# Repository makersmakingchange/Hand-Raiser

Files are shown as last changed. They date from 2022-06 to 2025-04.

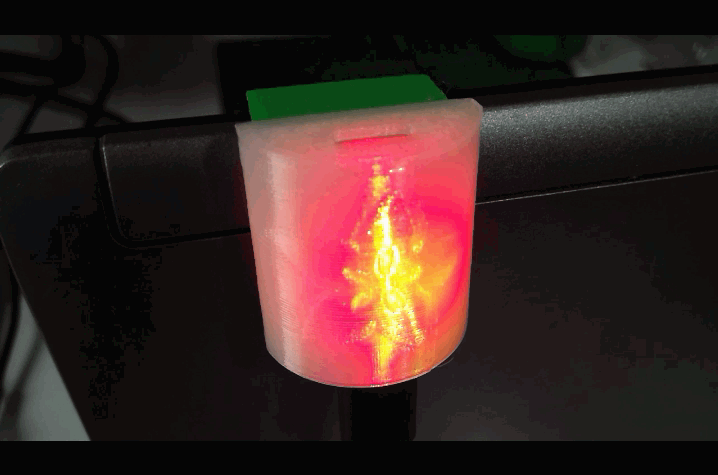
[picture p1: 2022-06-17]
Photos/Light on.PNG

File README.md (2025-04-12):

# Hand-Raiser
An assistive device used to catch the attention of a professor: an alternative to a student having to raise their hand.

Light on

## More info at
- [Makers Making Change Project Page]( https://makersmakingchange.com/project/hand-raiser/)
- [Adafruit Learning Guide](https://learn.adafruit.com/AT-Hand-Raiser)

## Getting Started
1. How to build this device

All of the files and instructions required to build the Hand-Raiser are contained within this repository. Refer to the Maker Checklist below.

2. How to request a build of this device

If you would like to obtain a Hand-Raiser but do not have the skills or equipment to do so, you may submit a build request through the [MMC Library Page](  https://makersmakingchange.com/project/hand-raiser/). The requestor is responsible for the cost of materials and any shipping.

3. How to build this device for someone else

If you have the skills and equipment to build this device, and would like to donate your time to create the switch for someone who needs it, visit the [MMC Maker Wanted](https://makersmakingchange.com/maker-wanted/) section.

## Files

### Documentation
| Document                     | Version | Link                                                                                  
|------------------------------|---------|--------------------------------------------------------------------------------|
| Maker Checklist              | 1.0     | [Maker Checklist](/Documentation/Hand-Raiser_Maker_Checklist.pdf)         |
| Bill of Materials            | 1.0     | [BOM](/Documentation/Working_Documents/Hand-Raiser_BOM.xlsx)                                |
| 3D Printing Guide            | 1.0     | [3D Printing Guide](Documentation/Hand-Raiser_3D_Print_Guide.pdf)      |
| Assembly Guide               | 1.0     | [Assembly Guide](/Documentation/Hand-Raiser_Assembly_Guide.pdf)           | 
| Maker Checklist              | 1.0     | [Maker Checklist](/Documentation/Hand-Raiser_Maker_Checklist.pdf)         |
| Adding Additional Colours    | 1.0     | [Adding Additional Colours](/Documentation/Hand-Raiser_How_to_Add_Additional_Colours.pdf)                  |
| User Quick Guide             | 1.0     | [User Guide](/Documentation/Hand-Raiser_User_Guide.pdf)                  |

## Attribution 

This device was designed by AT Makers.
The code for this device was written by Bill Binko and is licensed under the MIT license.
The Hand-Raiser 3D printed housing was designed by AT Makers and is licensed under the Creative Commons - Attribution - Non-Commercial - Share Alike license.
Documentation for this device was created by Neil Squire / Makers Making Change licensed under the CC-BY-SA 4.0 license.

## License 
Everything needed or used to design, make, test, or prepare the Hand Raiser is licensed under the CERN 2.0 Permissive license <https://ohwr.org/project/cernohl/wikis/Documents/CERN-OHL-version-2> (CERN-OHL-P) . 

Accompanying material such as instruction manuals, videos, and other copyrightable works that are useful but not necessary to design, make, test, or prepare the Hand Raiser are published under a Creative Commons Attribution-ShareAlike 4.0 license <https://creativecommons.org/licenses/by-sa/4.0/> (CC BY-SA 4.0) 

 ----

<!-- ABOUT MMC START -->
## About Makers Making Change
[Makers Making Change Logo](https://www.makersmakingchange.com/)

Makers Making Change is a program of [Neil Squire](https://www.neilsquire.ca/), a Canadian non-profit that uses technology, knowledge, and passion to empower people with disabilities.

Makers Making Change leverages the capacity of community based Makers, Disability Professionals and Volunteers to develop and deliver affordable Open Source Assistive Technologies.

 - Website: [www.MakersMakingChange.com](https://www.makersmakingchange.com/)
 - GitHub: [makersmakingchange](https://github.com/makersmakingchange)
 - Bluesky: [@makersmakingchange.bsky.social](https://bsky.app/profile/makersmakingchange.bsky.social)
 - Instagram: [@makersmakingchange](https://www.instagram.com/makersmakingchange)
 - Facebook: [makersmakechange](https://www.facebook.com/makersmakechange)
 - LinkedIn: [Neil Squire Society](https://www.linkedin.com/company/neil-squire-society/)
 - Thingiverse: [makersmakingchange](https://www.thingiverse.com/makersmakingchange/about)
 - Printables: [MakersMakingChange](https://www.printables.com/@MakersMakingChange)

### Contact Us
For technical questions, to get involved, or to share your experience we encourage you to [visit our website](https://www.makersmakingchange.com/) or [contact us](https://www.makersmakingchange.com/s/contact).
<!-- ABOUT MMC END -->

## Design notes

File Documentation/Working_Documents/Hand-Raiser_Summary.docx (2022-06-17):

### Title

Hand-Raiser

### Subtitle

An assistive device used to catch the attention of a professor: an alternative to a student having to raise their hand.

### Device Specifications

Build Time:

< 1hr

1-4 hr

5-10hr

>10hr

Cost:

$0 - $10

$11 - $25

$26 - $50

$51 - $100

$101 - $250

$250+

Stage: Recently Added

Skills: 3D Printing, Software

Need: Mobility

Disability: Mobility/Physical

Difficulty: Beginner

License:

Usages: Aids for Daily Living (ADL), Mobility, Communications Aids (AAC)

Type:

Designer: AT Makers

## Device Details

### Overview

The Hand-Raiser is an assistive device intended to be used to catch the attention of a professor without a student having to raise their hand. This device would be beneficial for someone who has difficulty or is unable to raise their hand for an extended period of time.

### Usage

The Hand-Raiser works by flashing it's light according to the incoming requests through the USB connection. The Hand-Raiser includes a set of Windows Shortcuts that can be used to change the LED by just double clicking on it.

### Compatibility

The Hand-Raiser can work with any PC, Mac, Android, or Raspberry Pi with a USB port.

### Cost

The Hand-Raiser costs approximately $15.

### Build Instructions

#### A set of build instructions can be found linked above in the Assembly Guide.

#### Skills Required

- 3D Printing Skills
- Programming

### Time Required

- Total print time: 70 minutes
- Assembly Time: 10 minutes

#### Tools

- 3D Printer
- Computer with USB port

#### Components

- 1x Adafruit Trinket - Link (https://www.adafruit.com/product/3500)
- 1x USB Cable - USB A to micro-B - Link (https://www.adafruit.com/product/592)

### 3D Printing

All components can be printed with no support at 20% infill with a 0.2mm layer height. There are 3 pieces to the enclosure: a back plate, a hanging hook, and a faceplate.

- 1x Back Plate
- 1x Hanging Hook
- 1x Faceplate - This piece must be printed with translucent filament.

Note that there are several versions of the hook and the faceplate, but you only need one of each.

### Attribution

The code for this device was written by Bill Binko and is licensed under the MIT license.

The Hand-Raiser 3D printed housing was designed by AT Makers (http://atmakers.org/2020/01/handraiser-light/) and is licensed under the Creative Commons - Attribution - Non-Commercial - Share Alike license.

Documentation for this device was created by Neil Squire / Makers Making Change licensed under the CC-BY-SA 4.0 license.

© 2022 by Neil Squire / Makers Making Change. This work is licensed under the CC BY SA 4.0 License: http://creativecommons.org/licenses/by-sa/4.0 Files available at https://makersmakingchange.com/project/hand-raiser/ Page 1 of 2

V1.0 | MAY 2021 Hand-Raiser Summary

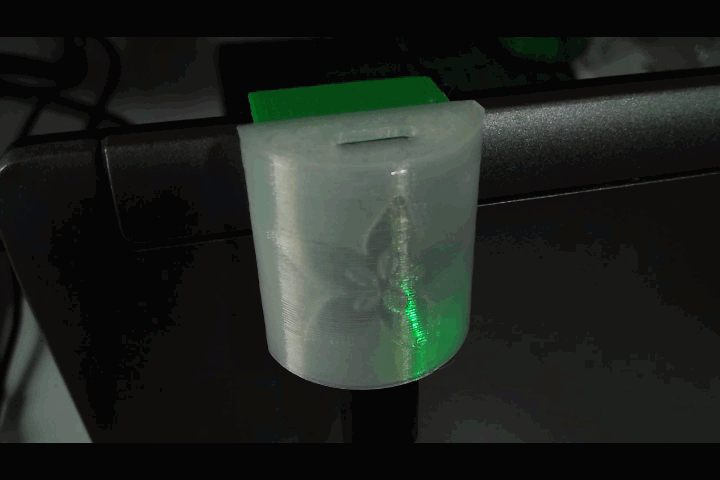
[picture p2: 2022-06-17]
Photos/trinket_Light3.gif

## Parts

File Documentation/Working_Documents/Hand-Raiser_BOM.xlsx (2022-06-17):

Device: Hand-Raiser |  | Total Cost | Total Print time (hr) | Total filament (g)
Version: V1.0 | Date Created: MAY 2022 | $12.15 | 1.17 | 10
Commercial Parts:
Part type (Electrical. Mechanical, Sanitization, ect) | Part Name | Quantity Needed | Pkg Quantity | Price per package | Price per Unit | Price for qty needed | Link
Microcontroller Board | Adafruit Trinket M0 | 1 | 1 | $8.95 | $8.95 | $8.95 | Adafruit Trinket M0 - for use with CircuitPython & Arduino IDE : ID 3500 : $8.95 : Adafruit Industries, Unique & fun DIY electronics and kits (https://www.adafruit.com/product/3500)
USB Cable | USB A to Micro-B | 1 | 1 | $2.95 | $2.95 | $2.95 | USB cable - USB A to Micro-B [3 foot long] : ID 592 : $2.95 : Adafruit Industries, Unique & fun DIY electronics and kits (https://www.adafruit.com/product/592)
3D Printed Parts ESTIMATED PRICING USING 1KG ROLL COST: | $25.00
Part | Description | Quantity Needed | TOTAL Mass (g) | Estimated Price | Print Time (Min) | Link
Snap Back | Piece that the micro controller snaps onto | 1 | 3 | $0.07 | 13
Snap Hanger | Piece used to hang the device | 1 | 3 | $0.07 | 21
Face Plate | Clear piece that covers LED light | 1 | 4 | $0.10 | 36
 |  |  | Total Print Cost: | $0.25
Tools for Assembly
Computer with Windows
Alternatives (if there are other sources for some parts link them below)
Part and description | Link

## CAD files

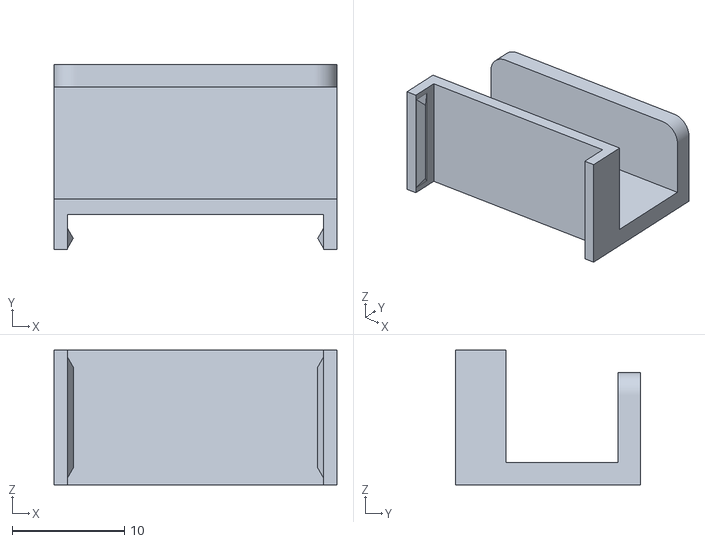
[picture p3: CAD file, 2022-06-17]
Build_Files/Snap_Hanger.stl
25.2 x 16.5 x 12.0

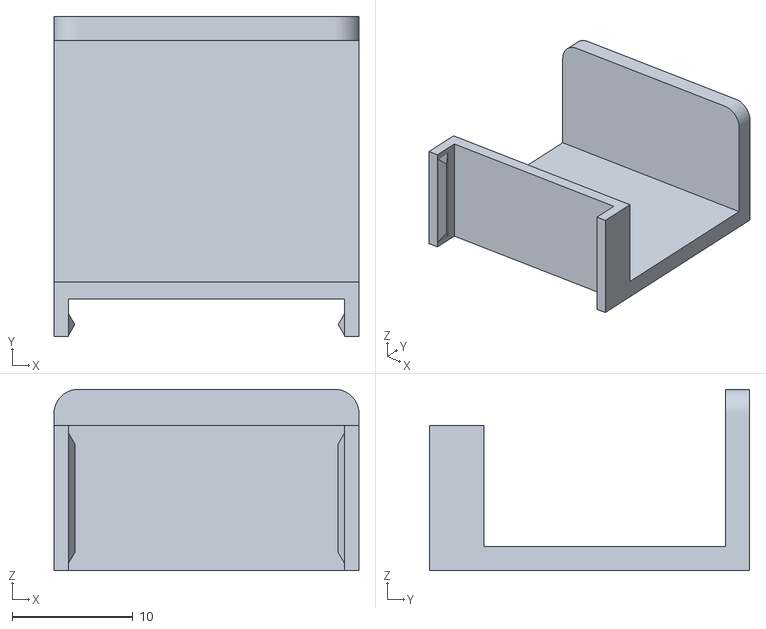
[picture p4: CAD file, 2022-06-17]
Build_Files/Snap_Hanger_20mm.stl
25.2 x 26.5 x 15.0

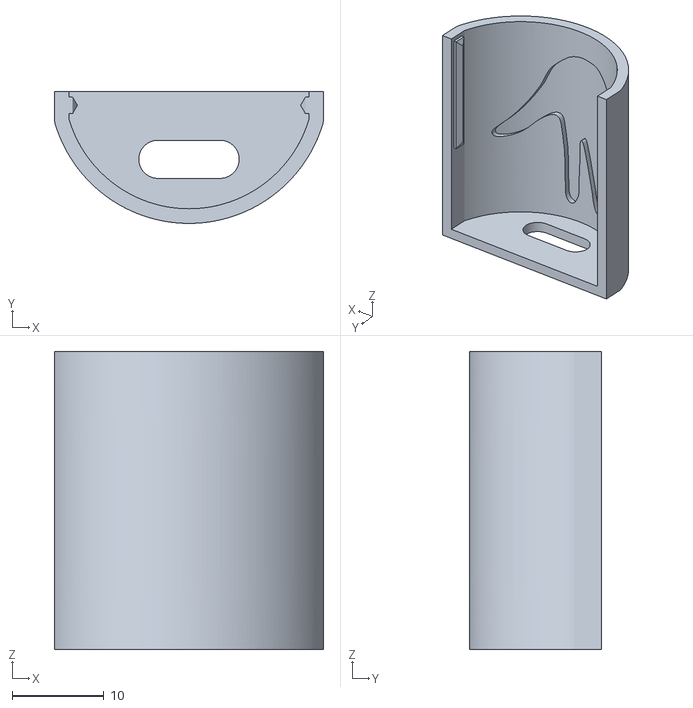
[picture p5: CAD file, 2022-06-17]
Build_Files/Faceplate-Hand.stl
29.4 x 14.4 x 32.6

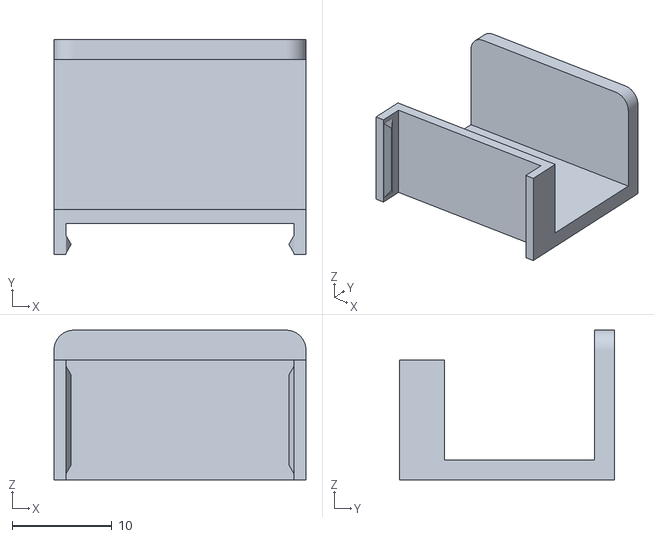
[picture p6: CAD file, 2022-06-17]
Build_Files/Snap_Hanger_15mm.stl
25.2 x 21.5 x 15.0

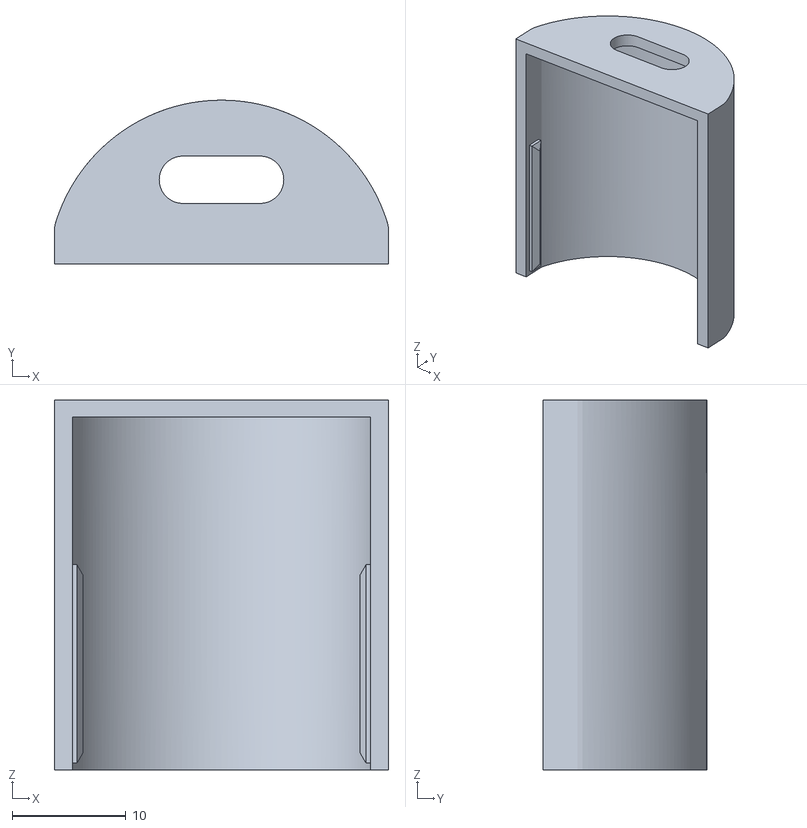
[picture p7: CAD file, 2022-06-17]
Build_Files/Faceplate-Blank.stl
29.4 x 14.4 x 32.6

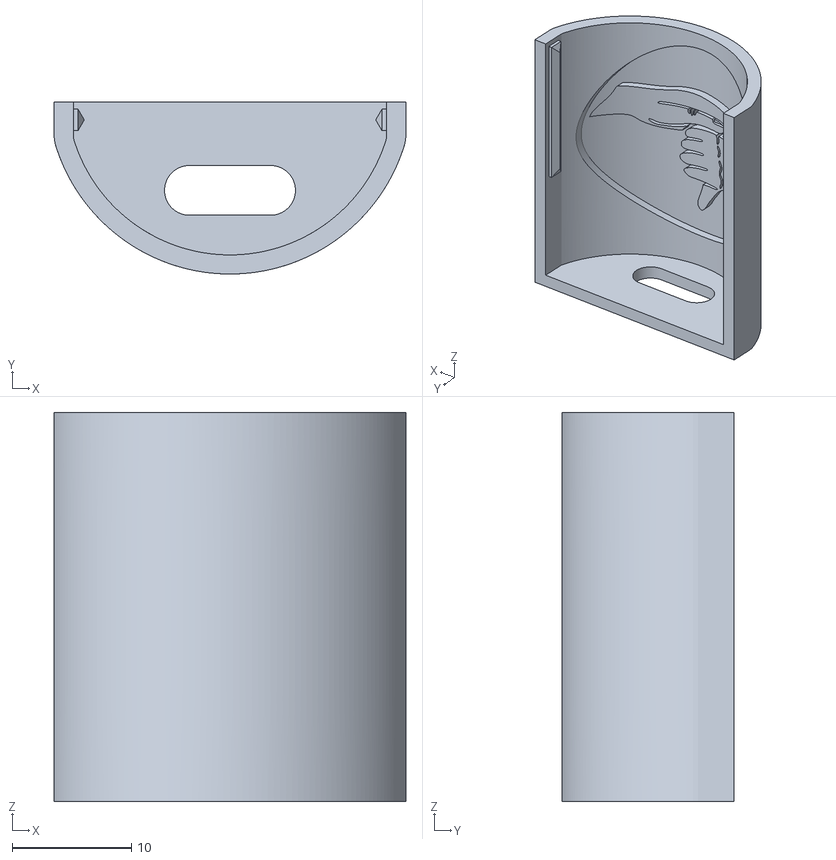
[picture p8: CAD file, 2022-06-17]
Build_Files/Faceplate-ATMakers.stl
29.4 x 14.4 x 32.6

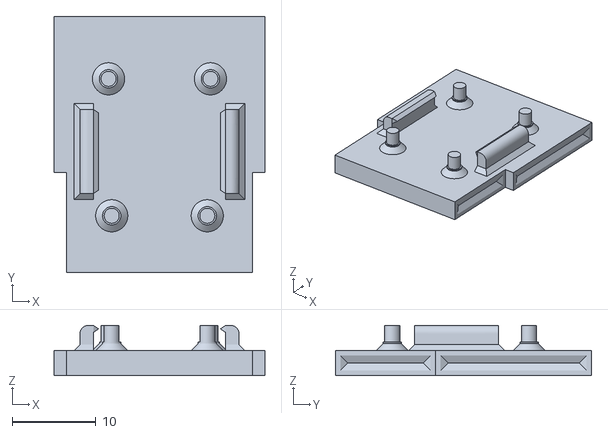
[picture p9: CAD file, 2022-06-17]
Build_Files/Snap_Back.stl
25.2 x 30.7 x 6.00

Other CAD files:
Build_Files/Faceplate-Adafruit.stl
Design_Files/Little_Handraiser.f3d

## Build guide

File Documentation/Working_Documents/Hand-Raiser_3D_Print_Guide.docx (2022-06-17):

# 3D Printing Summary

Metrics | HandRaiser with 15mm Snap Hanger | HandRaiser with 20mm Snap Hanger
Total Print Time (min) | 69 | 69
Total Number of Components | 3 | 3
Typical Total Mass (g) | 10 | 10
Typical Number of Print Setups | 2 | 2

# 3D Printing Settings

Print File Name | Qty | Total Print Time (hr:min) | Mass (g) | Infill (%) | Support (Y/N) | Layer Height/ Nozzle Diameter(mm) | Notes (orientation, special settings, etc)
Snap_Back.stl | 1 | 0:12 | 3 | 20 | N | 0.2/0.4 | Print in orientation given in STL
Snap_Hanger.stl (10mm) | 1 | 0:17 | 3 | 20 | N | 0.2/0.4 | Print in orientation given in STL
Snap_Hanger_15mm.stl | 1 | 0:21 | 3 | 20 | N | 0.2/0.4 | Print in orientation given in STL
Snap_Hanger_20mm.stl | 1 | 0:21 | 3 | 20 | N | 0.2/0.4 | Print in orientation given in STL
Faceplate-Blank.stl | 1 | 0:36 | 4 | 20 | N | 0.2/0.4 | Print in orientation given in STL
Faceplate-ATMakers.stl | 1 | 0:36 | 4 | 20 | N | 0.2/0.4 | Print in orientation given in STL
Faceplate-Hand.stl | 1 | 0:36 | 4 | 20 | N | 0.2/0.4 | Print in orientation given in STL
Faceplate-Adafruit.stl | 1 | 0:36 | 4 | 20 | N | 0.2/0.4 | Print in orientation given in STL

# Post-Processing

The Hand-Raiser is printed without supports; hence no post-processing is required.

# Customization Options

The Hand-Raiser can be printed with different sized hangers depending on which size works best for the user. There are .stl files for a 10mm (1), 15mm (2) and a 20mm hanger (3), but the. f3d file can be modified to accommodate other sized hangers if needed. The hand raiser can also be printed with different designs on the faceplate. The faceplate can be printed with an outline of a hand (4), an adafruit (5), the ATMakers symbol (6) or plain (7) as faintly shown below. Other customizations include printing the device in different colours.

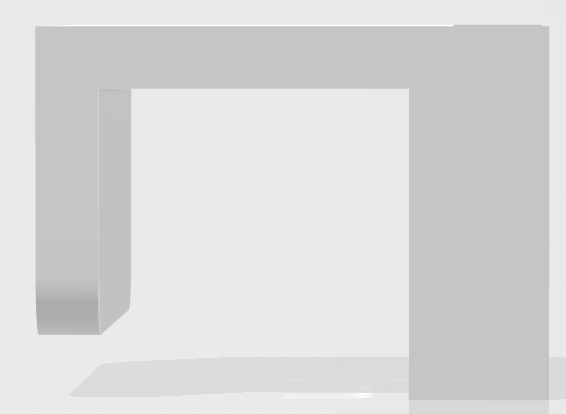
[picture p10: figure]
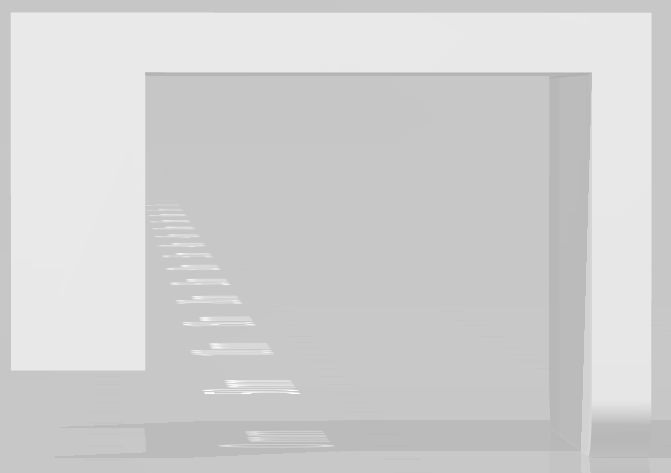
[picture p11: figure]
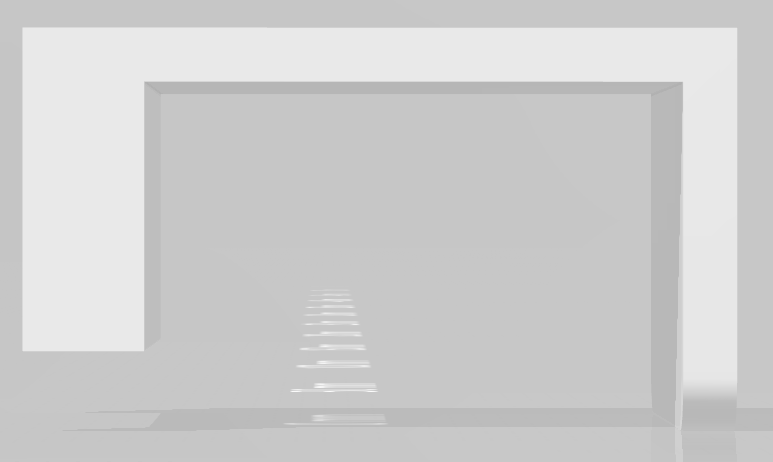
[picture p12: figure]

(1) 10cm Hanger | (2) 15mm Hanger | (3) 20mm Hanger

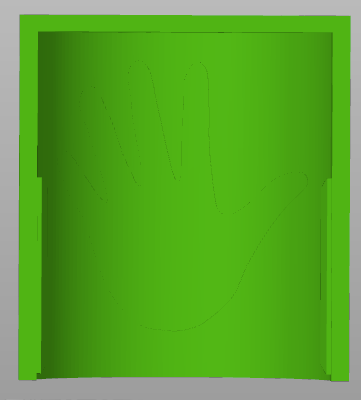
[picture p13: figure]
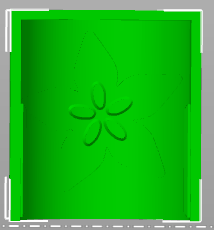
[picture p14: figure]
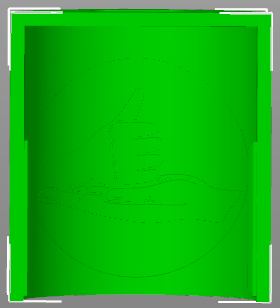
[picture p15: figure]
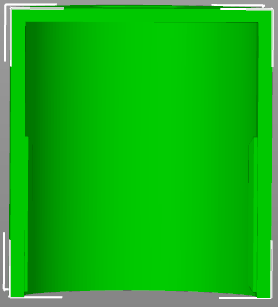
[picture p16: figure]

| (4) Hand | (5) Adafruit | (6) ATMakers | (7) Blank

# Examples of Quality Prints

Below is a picture of what quality is expected from printing the device.

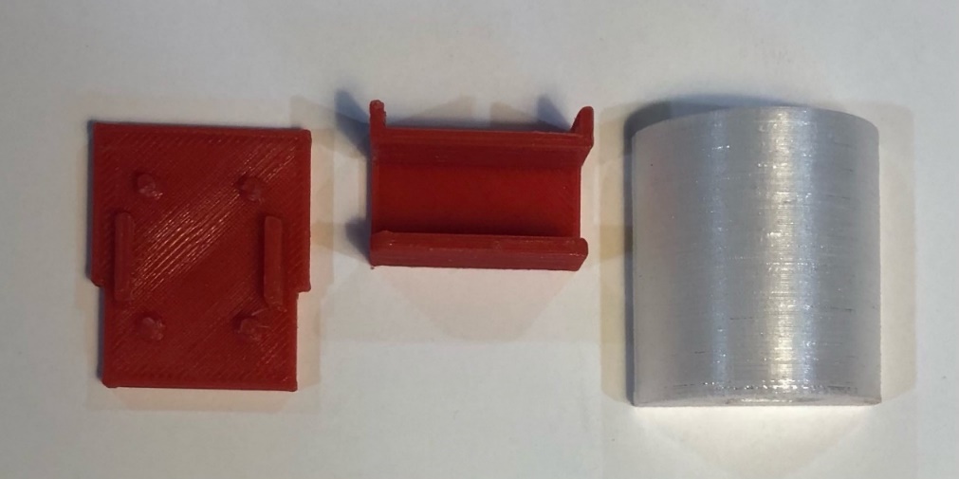
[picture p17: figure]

© 2022 by Neil Squire / Makers Making Change. This work is licensed under the CC BY SA 4.0 License: http://creativecommons.org/licenses/by-sa/4.0 Files available at https://makersmakingchange.com/project/hand-raiser/ Page 1 of 2

V1.0 | MAY 2022 Hand-Raiser 3D Printing Guide

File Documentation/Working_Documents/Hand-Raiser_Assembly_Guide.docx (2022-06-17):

# Required Components

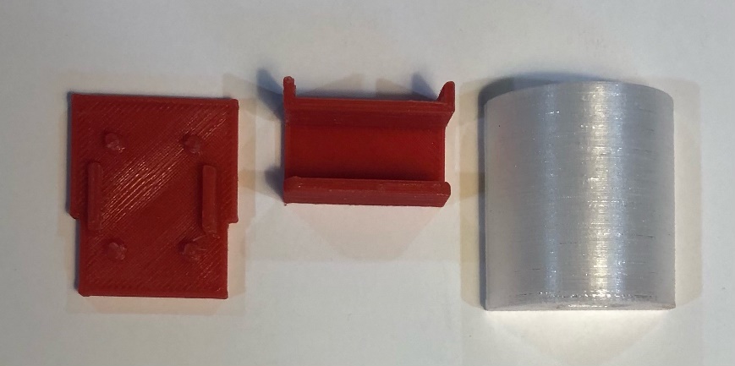
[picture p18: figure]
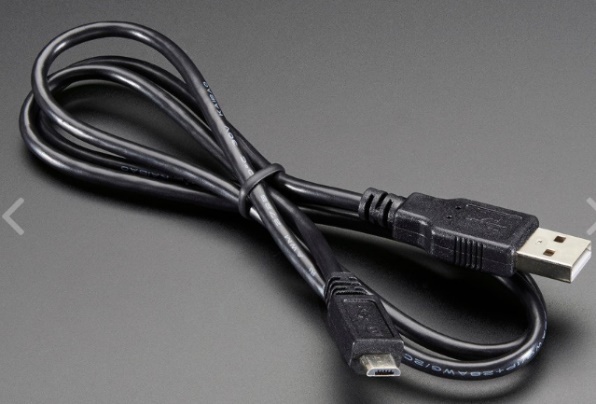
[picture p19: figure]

2 3 1 4 | BOM 1 1x 3D Printed Snap Back 2 1x 3D Printed Snap Hanger 3 1x 3D Printed Face Plate 4 1x USB Cable – USB A to USB Micro

# Required Tools

- Computer with Windows.

# Programming the Trinket

## Step 1

Download the HandRaiser.UF2 file. https://github.com/ATMakersOrg/Little-HandRaiser/raw/master/LittleHandRaiser.UF2

## Step 2

Carefully plug the Trinket into your USB port in your computer.

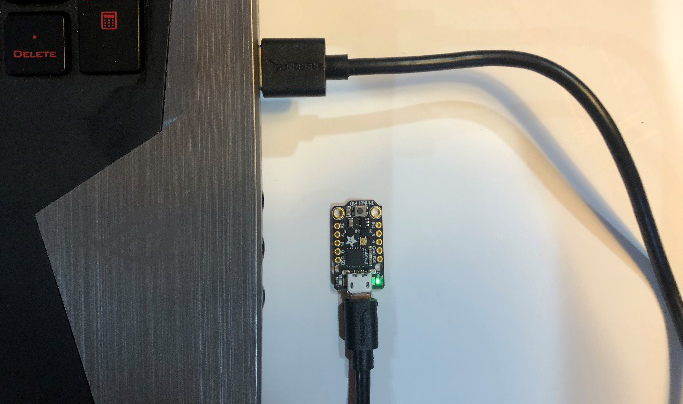
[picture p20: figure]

## Step 3

Put the Trinket in Bootloader Mode by double clicking the Reset Button. The LED light should blink green.

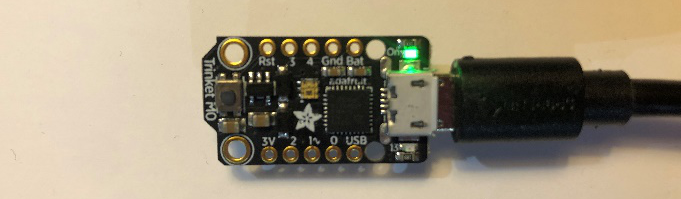
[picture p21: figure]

## Step 4

Locate the new drive named TRINKETBOOT (F:).

## Step 5

Copy the HandRaiser.UF2 file to that drive. The Trinket will restart, and the drive should be renamed to CIRCUITPY.

## Step 6

The Windows Commands can now be used to activate the device.

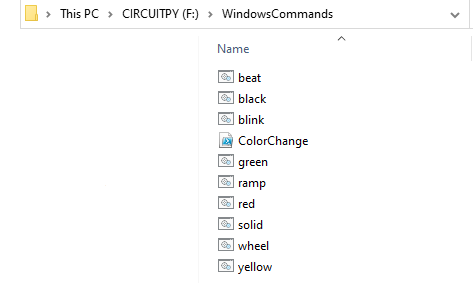
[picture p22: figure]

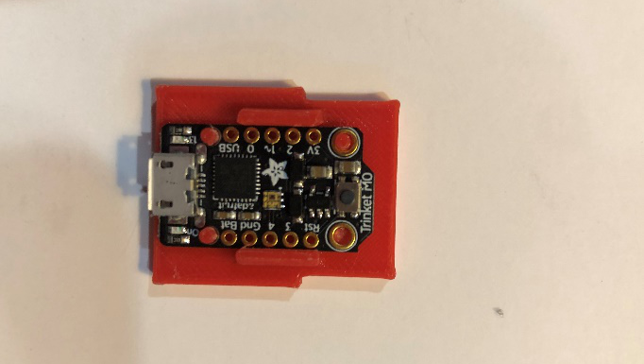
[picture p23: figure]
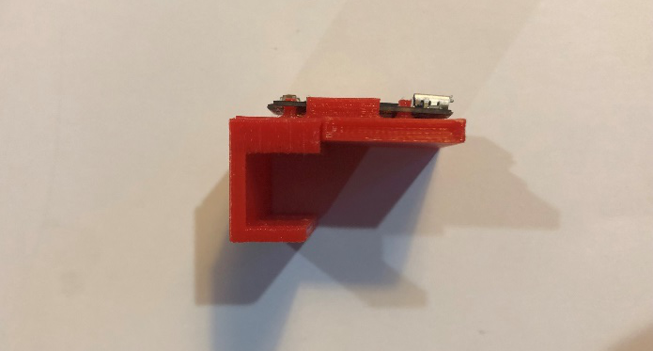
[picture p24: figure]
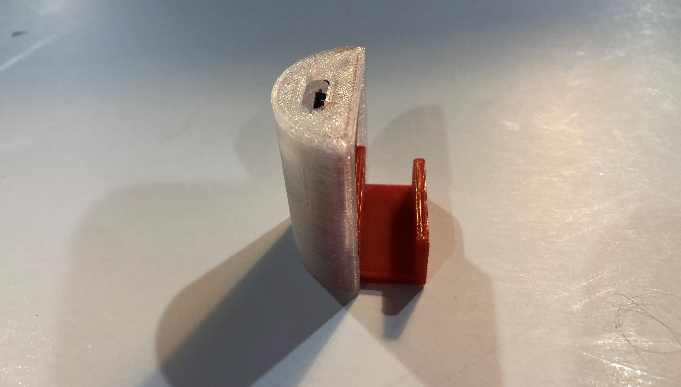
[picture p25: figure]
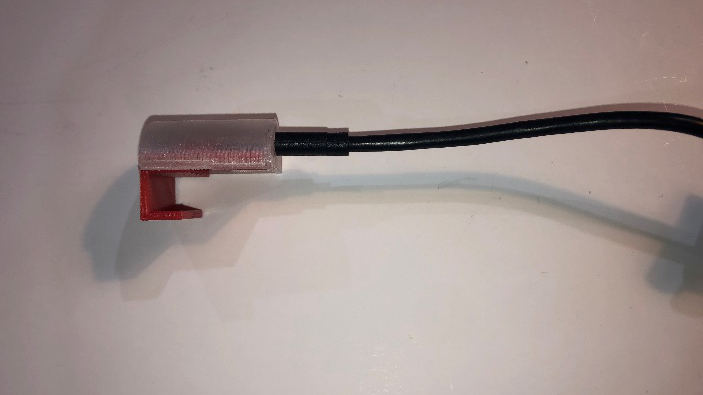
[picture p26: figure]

Assembly Instructions Step 1 Align the 4 holes on the Trinket M0 with the Snap Back. Make sure the micro-USB port is pointed towards the wider end of the print. Firmly press it on. Step 2 Snap on the Hanger onto the Snap Back using the snap-fit grooves. Step 3 Snap on the cover. Make sure the end with the hole aligns with the micro-USB port. Step 4 Carefully plug the micro-USB cable into the Trinket.

© 2022 by Neil Squire / Makers Making Change. This work is licensed under the CC BY SA 4.0 License: http://creativecommons.org/licenses/by-sa/4.0 Files available at https://makersmakingchange.com/project/hand-raiser/ Page 1 of 1

V1.0 | MAY 2022 Hand-Raiser ASSEMBLY GUIDE

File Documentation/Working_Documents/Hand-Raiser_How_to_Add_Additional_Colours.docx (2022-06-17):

# Overview

Once the Hand-Raiser is programmed, it automatically comes with red, yellow, and green light shortcuts. If the user wants additional colour shortcuts added onto the device, this document can be used to explain how to do so with a Windows computer.

# Adding Additional Colours on Windows

## Step 1

In the search bar, locate and open the Notepad App.

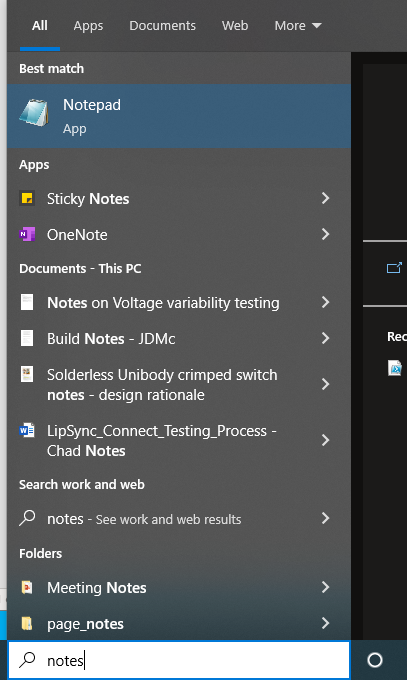
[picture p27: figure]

## Step 2

Type powershell -executionpolicy bypass -File "ColorChange.ps1" "#" into the NotePad as well the 6 digit Hex code following the # of the colour you are trying to achieve. A hex code for any colour can be found here: link (https://www.rapidtables.com/web/color/html-color-codes.html). For example, the #ff00ff below is the Hex code for a pink.

## Step 3

Next, in the top left corner of the Notepad, press File -> Save as. The window below should pop up. Make sure you save this short cut in CIRCUITPY (F:) -> WindowsCommands. When naming the file, make sure you name it with a .bat following the name. For example, shown below is the file named pink.bat. Next, ensure under the Encoding tab that ANSI is selected.

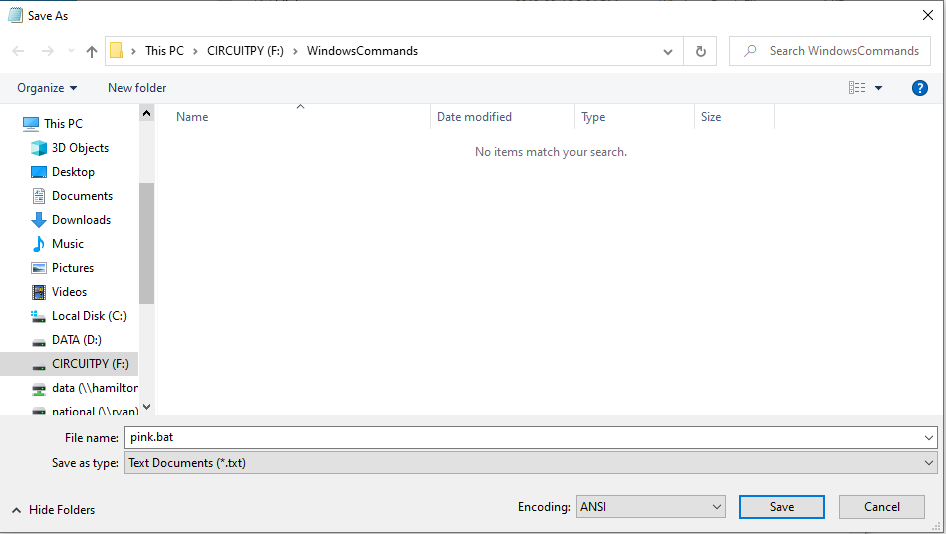
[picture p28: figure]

## Step 4

Open up Files -> CIRCUITPY (F:) -> WindowsCommands to see if the new colour is there. Next, you can double click on the colour to check that it works. Sometimes the hex code colours do not come out exactly how they appear online and will have to be modified to achieve the colour that you are looking for.

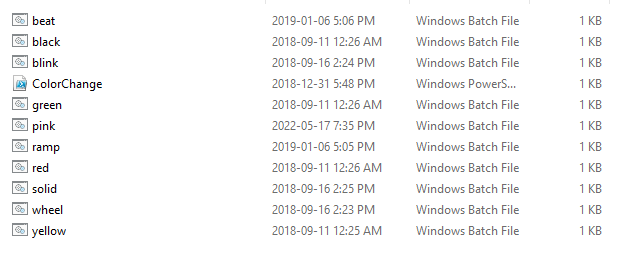
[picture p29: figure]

© 2022 by Neil Squire / Makers Making Change. This work is licensed under the CC BY SA 4.0 License: http://creativecommons.org/licenses/by-sa/4.0 Files available at https://makersmakingchange.com/project/hand-raiser/ Page 1 of 4

V1.0 | MAY 2022 Hand-Raiser hOW TO ADD ADDITIONAL COLOURS

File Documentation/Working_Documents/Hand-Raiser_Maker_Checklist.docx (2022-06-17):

# Maker To Do List

- Ask the requestor if they want any customizations to the device (e.g., colour, which size hanger they want, which design on the faceplate they want, etc.)
- Determine the cost of materials and relay this cost to the user before printing to ensure the requester is comfortable with the price.
- Tell the user that red, yellow, and green LED shortcuts come programmed on the Hand-Raiser. Ask the user if there are any additional colours that they would like programmed. They can have any colors that are in the Color Hexadecimal System. If they want to pick custom colors, send them this link to the Hex Calculator: Colors HEX (w3schools.com) (https://www.w3schools.com/colors/colors_hexadecimal.asp).
- Order the Adafruit Trinket and USB Cable.
- Make sure that you have a translucent filament as well as a regular filament.
- Build the Hand-Raiser.
- Program the Adafruit Trinket.
- Add shortcuts to any additional colours requested by the user. Test the new colours to ensure they are close to what the user expected from the Hex Calculator. Not every colour translates perfectly so you might have to tweak the Hex code.

# Items to Give to User

- User Guide.
- Hand-Raiser.
- USB cable.

© 2022 by Neil Squire / Makers Making Change. This work is licensed under the CC BY SA 4.0 License: http://creativecommons.org/licenses/by-sa/4.0 Files available at https://makersmakingchange.com/project/hand-raiser/ Page 1 of 1

V1.0 | MAY 2022 Hand-Raiser Maker Checklist

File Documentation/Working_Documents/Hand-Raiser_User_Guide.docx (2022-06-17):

## Introduction

The Hand-Raiser is an assistive device used to catch the attention of a professor without a student having to raise their hand. This device would be beneficial for someone who has difficulty or is unable to raise their hand for an extended period of time.

## Features

This device can flash different colour LED lights at different brightness levels and in different patterns. In the below figures, the LED light is red and is flashing on (A) and off (B).

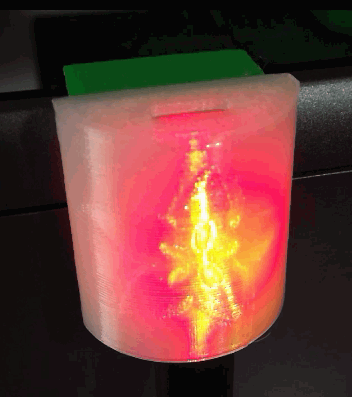
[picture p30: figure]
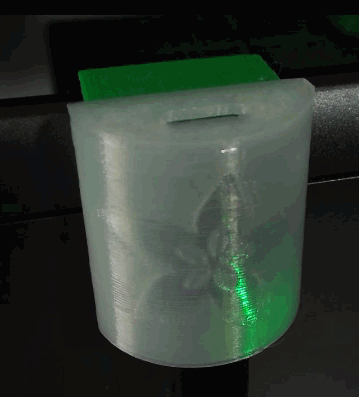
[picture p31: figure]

A | B

## Usage

The Hand-Raiser works by listening to the incoming requests through the USB connection. The Hand-Raiser includes a set of Windows Shortcuts that can be used to change the LED by just double clicking on them.

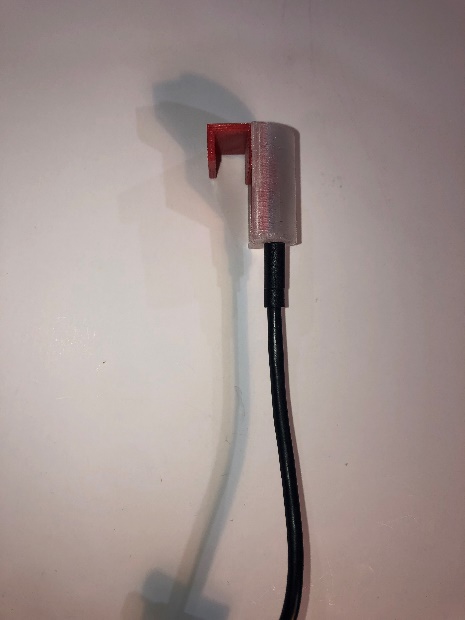
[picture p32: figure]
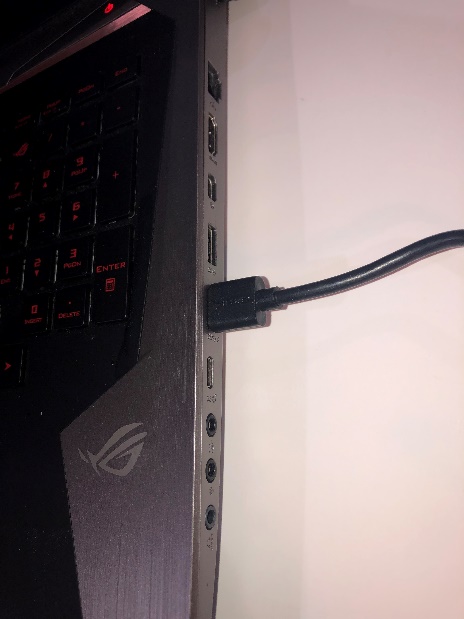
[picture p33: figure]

How to Use the Hand-Raiser Step 1 Carefully plug the USB cable into the Hand-Raiser. | Step 2 Plug the other end of the USB cable into the desired device.

### Step 3

Hang the Hand-Raiser on the back of the laptop or any other desired location.

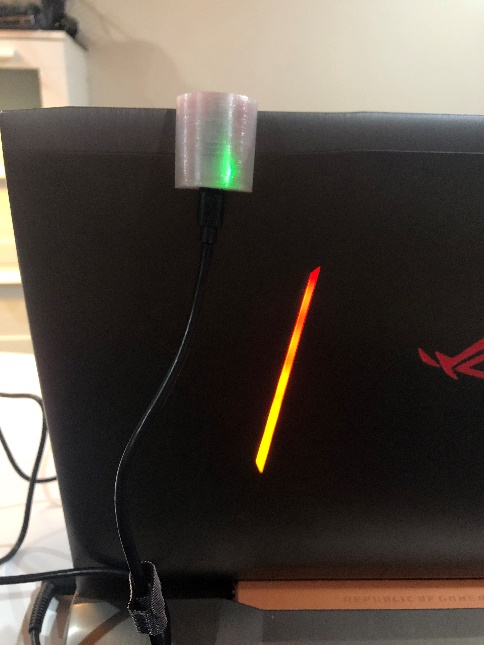
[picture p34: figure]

### Step 4

In Files, locate and open the Hand-Raiser called CIRCUITPY (F:) , then open WindowsCommands. You will see listed all the colours and flashing patterns that are on the Hand-Raiser. If you want to display a colour or a pattern, you have to double click on each. For example, if you want a blinking red light, double click the “blinking” file, then double click the “red” file. If you then wanted to switch to a blinking yellow light, you would just double click on the “yellow” file.

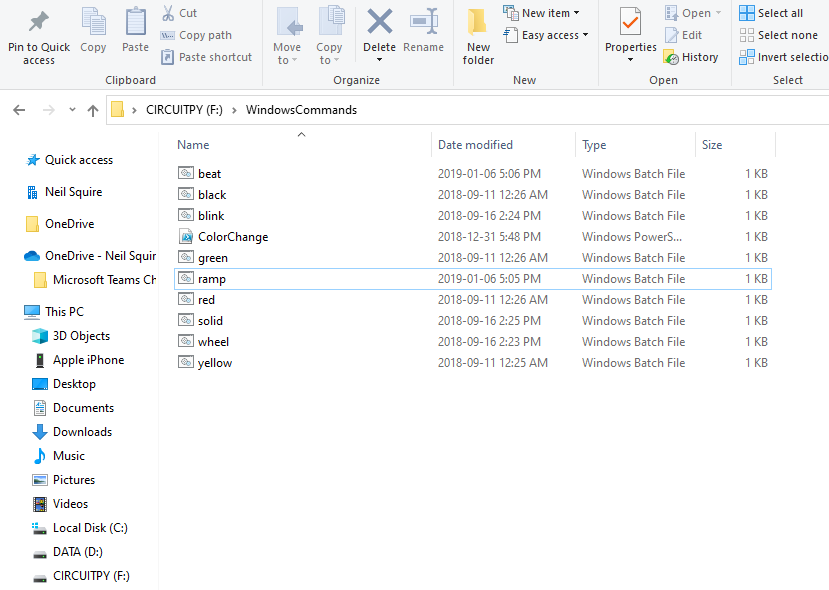
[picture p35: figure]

### Step 5

To get the Hand-Raiser to stop flashing, double click on the “black” file.

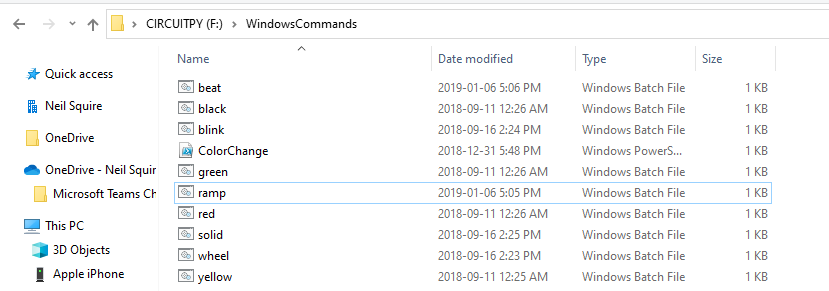
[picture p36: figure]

## Compatibility

The Hand-Raiser can work with any computer with Windows.

## Specifications

There are several versions of the hook and the faceplate, so the specifications listed below are specific to the 15mm Snap Hanger, the Blank Faceplate, and the Snap Back. The specifications for the other hooks and faceplates are very similar to the ones mentioned. X Y and Z directions are determined when the 3D components are in the orientation that does not require the components to be printed with supports. The X direction is defined as the shorter of the 2 planes parallel to the print bed, Y is defined as the longer of the 2 planes parallel to the print bed, and Z is defined as the height of the print off the print bed.

| Mass (g) | Dimensions (mm)
| | Length | Width | Height
15mm Snap Hanger | 3 | 22 | 30 | 12
Blank Faceplate | 4 | 14 | 29 | 33
Snap Back | 3 | 25 | 39 | 8

## Cleaning

The Hand-Raiser can be wiped down with sanitizing cleaners. Do not wash the Hand-Raiser in high heat as it may cause it to melt or could damage the electronics inside (i.e., do not put it in the dishwasher, the washing machine, or soak it in hot water).

© 2022 by Neil Squire / Makers Making Change. This work is licensed under the CC BY SA 4.0 License: http://creativecommons.org/licenses/by-sa/4.0 Files available at https://makersmakingchange.com/project/hand-raiser/ Page 1 of 3

V1.0 | MAY 2022 HAND-RAISER user Quick Guide

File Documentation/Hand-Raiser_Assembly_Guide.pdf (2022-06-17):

V1.0 | MAY 2022

# Hand-Raiser

# ASSEMBLY GUIDE

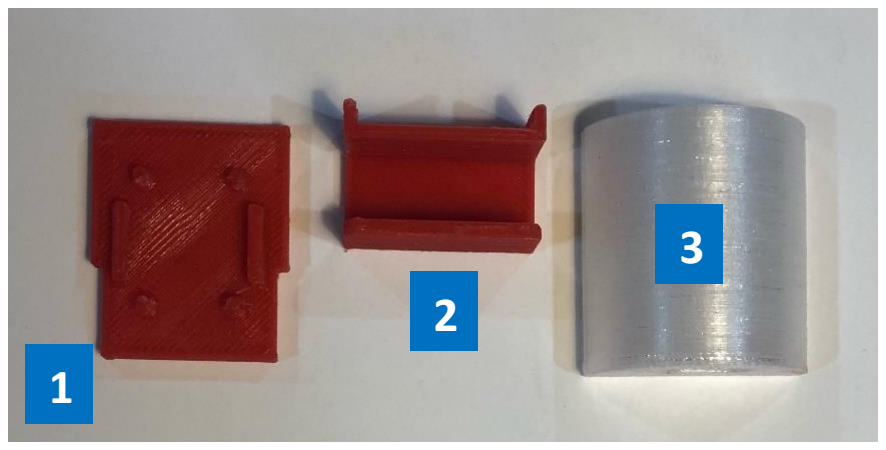
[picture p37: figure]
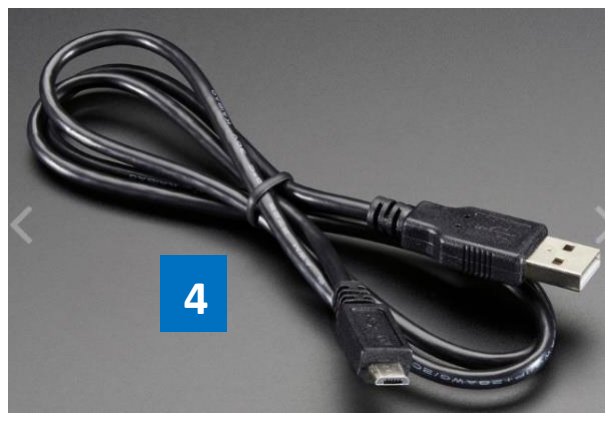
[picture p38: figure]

© 2022 by Neil Squire / Makers Making Change. This work is licensed under the CC BY SA 4.0 License: http://creativecommons.org/licenses/by-sa/4.0
Files available at https://makersmakingchange.com/project/hand-raiser/ | Page 1 of 5

# Required Components

## BOM

## 1x 3D Printed Snap Back

## 1x 3D Printed Snap Hanger

## 1x 3D Printed Face Plate

## 1x USB Cable – USB A to USB Micro

# Required Tools

- Computer with Windows.

1

2

3

4

# ASSEMBLY GUIDE

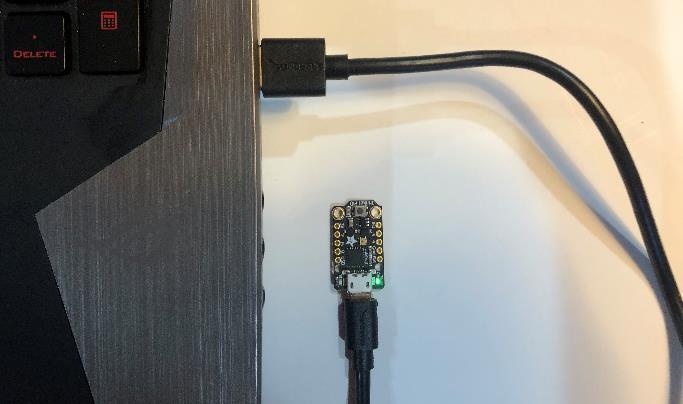
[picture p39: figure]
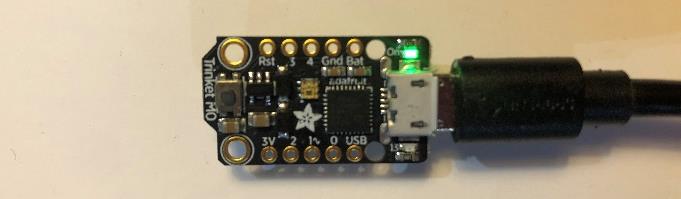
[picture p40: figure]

Files available at https://makersmakingchange.com/project/hand-raiser/ | Page 2 of 5

# Programming the Trinket

## Step 1

## Download the HandRaiser.UF2 file. https://github.com/ATMakersOrg/Little-HandRaiser/raw/master/LittleHandRaiser.UF2

## Step 2

Carefully plug the Trinket into your USB port in your computer.

## Step 3

Put the Trinket in Bootloader Mode by double clicking the Reset Button. The LED light should blink green.

## Step 4

Locate the new drive named TRINKETBOOT (F:).

# ASSEMBLY GUIDE

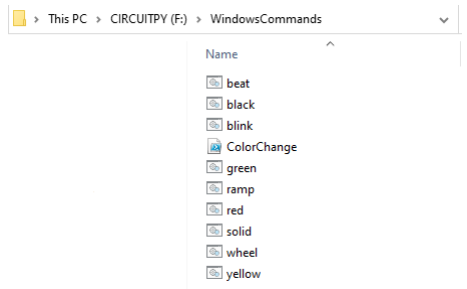
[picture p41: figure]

Files available at https://makersmakingchange.com/project/hand-raiser/ | Page 3 of 5

## Step 5

Copy the HandRaiser.UF2 file to that drive. The Trinket will restart, and the drive should be renamed to CIRCUITPY.

## Step 6

The Windows Commands can now be used to activate the device.

# ASSEMBLY GUIDE

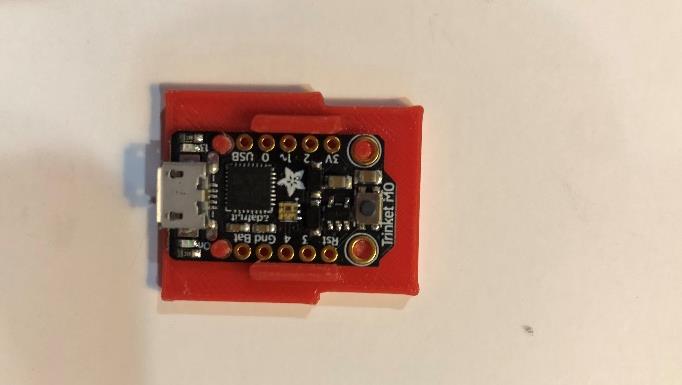
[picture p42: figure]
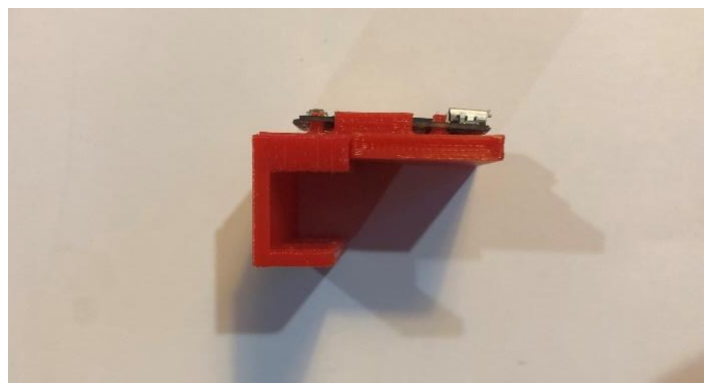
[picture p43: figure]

Files available at https://makersmakingchange.com/project/hand-raiser/ | Page 4 of 5

# Assembly Instructions

## Step 1

Align the 4 holes on the Trinket M0 with the Snap Back. Make sure the micro-USB port is pointed towards the wider end of the print. Firmly press it on.

## Step 2

Snap on the Hanger onto the Snap Back using the snap-fit grooves.

# ASSEMBLY GUIDE

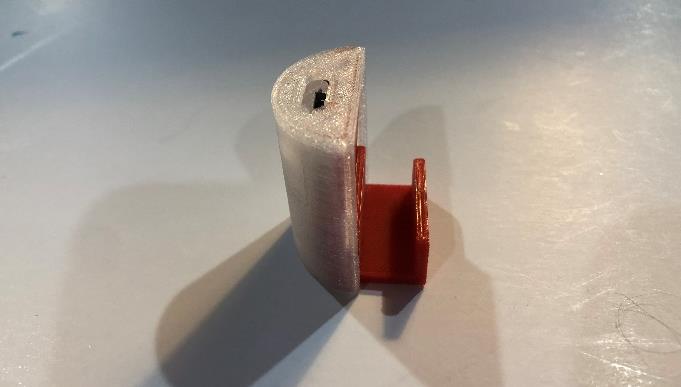
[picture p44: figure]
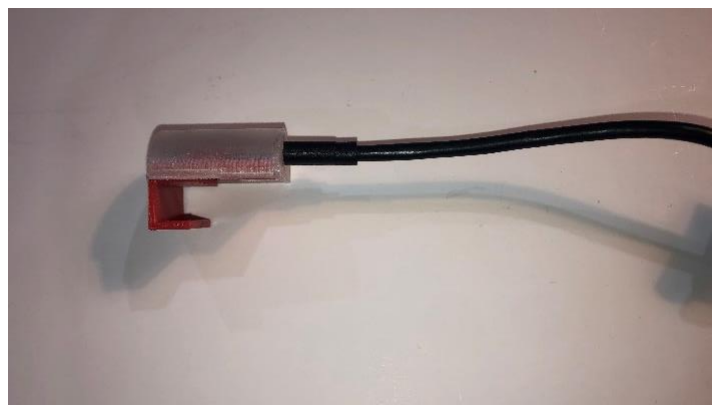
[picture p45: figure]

Files available at https://makersmakingchange.com/project/hand-raiser/ | Page 5 of 5

## Step 3

Snap on the cover. Make sure the end with the hole aligns with the micro-USB port.

## Step 4

Carefully plug the micro-USB cable into the Trinket.
